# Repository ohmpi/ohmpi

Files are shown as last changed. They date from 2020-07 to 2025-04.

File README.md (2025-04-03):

# OhmPi

Development of a low-cost multi-electrodes resistivity meter for electrical resistivity mesaurement for lab applications, based on raspberry board.

Join the community on [Discord](https://discord.gg/2SCKQZBzXh) to share your experience and provide feedback or use the gitlab issue.

## Installation

1. Download a .zip of this repository (or use `git clone https://gitlab.com/ohmpi/ohmpi.git`)
2. Enter the repository (`cd path/to/ohmpi`) and install the software needed. We made a simple script to make it simpler:

`./install.sh`

The installation script will create a virtual python environement `ohmpy` (with a 'y' at the end) where all packages specified in *requirements.txt* will be installed. The script also takes care of creating a configuration for your hardware if you wish.

To activate the environment and set the necessary `$PYTHONPATH` variable, you can use:

`source env.sh`

More examples are provided in the **[documentation](https://ohmpi.gitlab.io/ohmpi/)**.

## Gallery

A few pictures of the components of the OhmPi. More in the [**DOCUMENTATION**](https://ohmpi.gitlab.io/ohmpi/)!

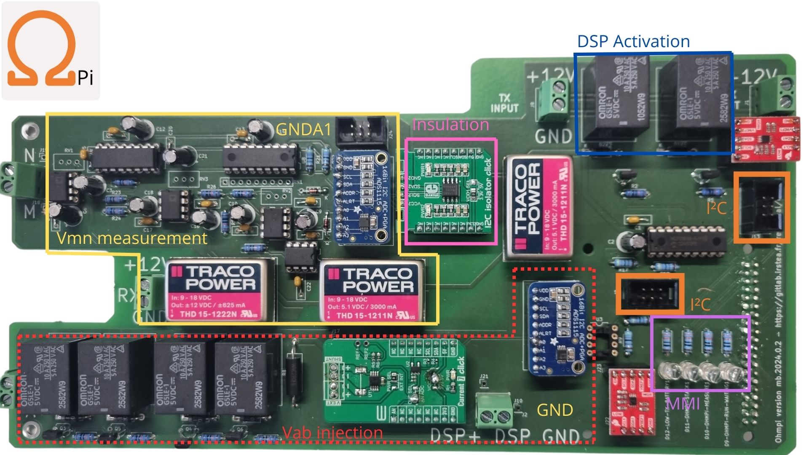
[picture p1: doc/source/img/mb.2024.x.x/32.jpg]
measurment board

*Measurement board (v2024).*

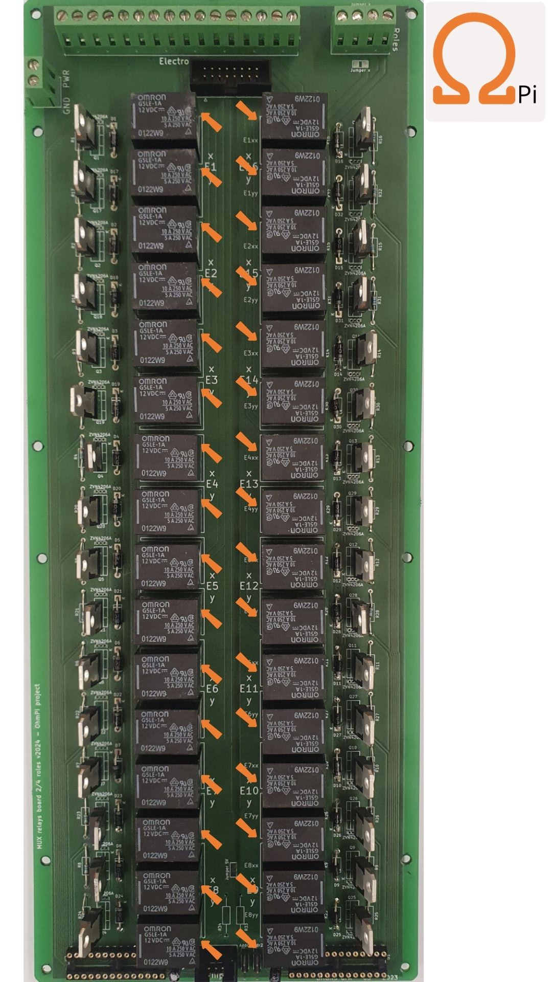
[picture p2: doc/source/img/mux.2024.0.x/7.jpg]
multiplexer board

*Multiplexer board (v2024).*

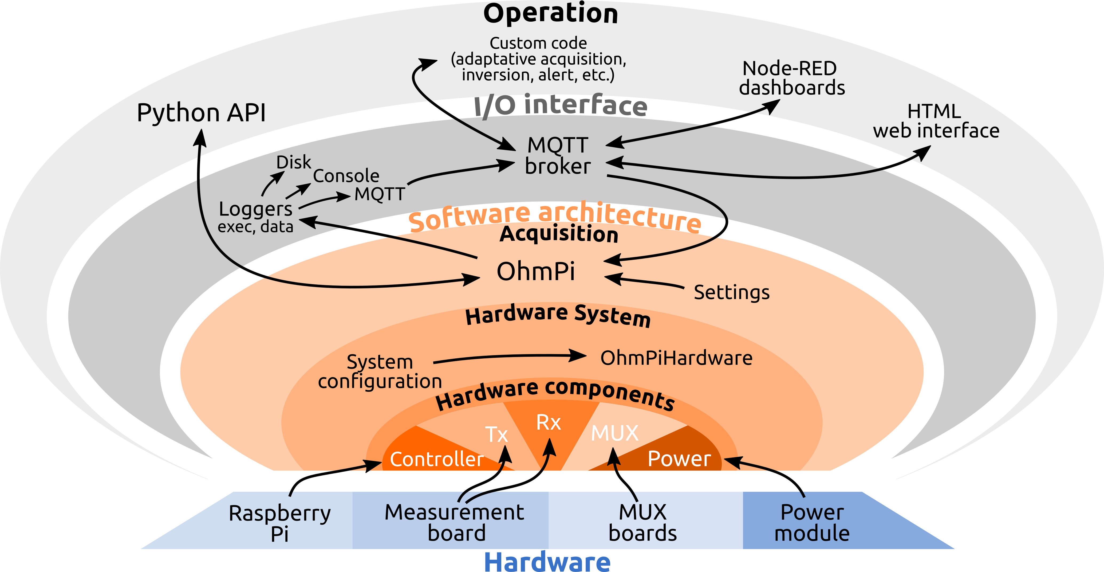
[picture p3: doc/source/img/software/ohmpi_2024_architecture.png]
software architecure

*Software architecture.*

## How to contribute

You can contribute to the code of OhmPi directly in this repository by raising issue or making merge request. We use different branches to manage different readiness level of the code:
- `issue_XXX` (e.g. `issue_240`) is a branch linked to an issue number to develop a new feature or fix a bug.
- `alpha`: experimental version of the code to be tested by core developers, this branch contains the latest changes but is **unstable**.
- `beta`: **testing** version, more stable than `alpha` that can be tried out by contributors to provide feedback to core developpers (released in winter). 
- `rc`: **release candidate** branch, version to be extensively tested before being released and merged into the `master` branch (released in spring).
- `master`: more **stable** version of the code. Bug fixes can be merged directly to master.

You can also contribute to the **documentation** (on the `docs` branch) by improving the documentation or showcasing your OhmPi application.

## Citing Ohmpi

If you use OhmPi for you work, please cite [this paper](https://www.sciencedirect.com/science/article/pii/S2468067220300316) as:

    Rémi Clement, Yannick Fargier, Vivien Dubois, Julien Gance, Emile Gros, Nicolas Forquet, OhmPi: An open source data logger for 
    dedicated applications of electrical resistivity imaging at the small and laboratory scale, HardwareX, Volume 8, 2020, e00122, ISSN 2468-0672, https://doi.org/10.1016/j.ohx.2020.e00122..

## License information

You may redistribute and modify this documentation and make products using it under the terms of the CERN-OHL-P v2 (https://cern.ch/cern-ohl). This documentation is distributed WITHOUT ANY EXPRESS OR IMPLIED WARRANTY, INCLUDING OF MERCHANTABILITY, SATISFACTORY QUALITY AND FITNESS FOR A PARTICULAR PURPOSE. Please see the CERN-OHL-P v2 for applicable conditions

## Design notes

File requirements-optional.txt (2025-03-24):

RPi.GPIO
adafruit-blinka
adafruit-circuitpython-ads1x15
adafruit-circuitpython-tca9548a
adafruit-circuitpython-mcp230xx
adafruit_extended_bus
minimalmodbus
gpiozero
numpy
paho-mqtt==1.6.1
urllib3
termcolor
pandas
matplotlib
scipy
requests
psutil
joblib

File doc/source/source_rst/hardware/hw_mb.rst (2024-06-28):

Measurement board
=============================

This section introduces the OhmPi measurement boards. Starting from this year, it has been possible to use any measurement board with the latest OhmPi code.
Consequently, the OhmPi group provides a variety of board options tailored to your technical needs (e.g., laboratory measurement, field measurement), budget, and electronic skills.

The characteristics of each measurement board are described in the following table:

Recognize the version of the measurement board
----------------------------------------------

   +-----------------------------------------------------------------+
   |   
   |      :width: 900px                                              |
   +-----------------------------------------------------------------+
   |**Measurement board V2023.0.1**                                  |
   +-----------------------------------------------------------------+
   |   
   |      :width: 900px                                              |
   +-----------------------------------------------------------------+
   |**Measurement board V2024.0.2**                                  |
   +-----------------------------------------------------------------+  

Specifications
--------------

.. table::
   :align: center

   +----------------------------------+-----------------------+-----------------------+-----------+
   | **Parameters**                   |**v2023.0.1**          |       **v2024.0.2**   | Units     |
   +==================================+=======================+=======================+===========+
   |Vmn number of channels            |1                      |1                      |-          |
   +----------------------------------+-----------------------+-----------------------+-----------+
   |Operating temperature             |0 to 50                |-25 to 50              |°C         |
   +----------------------------------+-----------------------+-----------------------+-----------+
   |Max. permissible Vab              |24                     |200                    |vdc        |
   +----------------------------------+-----------------------+-----------------------+-----------+
   |Power supply                      |12                     |12                     |vdc        |
   +----------------------------------+-----------------------+-----------------------+-----------+
   |Current with 2 ohms shunt resistor|0.11 to 40             |0.11 to 500            |mA         |
   +----------------------------------+-----------------------+-----------------------+-----------+
   |Min pulse duration                |50                     |50                     |ms         |
   +----------------------------------+-----------------------+-----------------------+-----------+
   |Max pulse duration                |15                     |15                     |second     |
   +----------------------------------+-----------------------+-----------------------+-----------+
   |Vmn input impedance               |80                     |1000                   |MOhm       |
   +----------------------------------+-----------------------+-----------------------+-----------+
   |Vmn range                         |-/+ 5                  | -/+5                  |volt       |
   +----------------------------------+-----------------------+-----------------------+-----------+

Assemble measurement board (MB)
------------------------------- 

.. toctree:: 
   :maxdepth: 2 

   mb/mb_2023.rst
   mb/mb_2024.rst

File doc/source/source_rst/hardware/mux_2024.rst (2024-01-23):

.. warning::
    **OhmPi is a participative project open to all, it requires skills in electronics and to respect the safety rules. OhmPi must be assembled in a professional context and by people competent in electronics. The OhmPi team cannot be held responsible for any material or human damage which would be associated with the use or the assembly of OHMPI. The OhmPi team cannot be held responsible if the equipment does not work after assembly.**

MUX board v2024
****************************************************

The MUX board v2024 uses the same technology than the MUX board v2023, i.e. mechanical multiplexing. However it introduces
a new level of flexibility by addressing multiple roles (A, B, M, N), which allows to build OhmPi system with multiple of 8 electrodes.
Users can physically configure the MUX board to address 2 roles (A, B or M, N) or 4 roles (A, B, M, N). With only 32 relays,
it can address 16 or 8 electrodes, for the 2- and 4-role configuration respectively.
Given the reduced number of relays, the MUX board v2024 is interfaced with only two MCP23017 I/O expanders.
This means that up to 4 MUX boards v2024 (i.e. 32-electrode system) can be directly connected to a measurement board v2024.
A newly introduced I2C extension board (featuring a TCA9548A multiplexer) allows to connect up to 32 MUX board v2024, equating to a 256-electrode system.
In theory, up to 8 I2C extension boards can be connected to the measurement board, which would allow to pilot 2048 electrodes.
For obvious practical reasons, such a configuration couldn't be tested and is likely to be limited by the I2C bus being phisically too long,
which would prevent to reach so many GPIOs.
In an effort to mitigate supply shortages, a last addition concerns the power mosfet associated with the relays,
with the possibility to mount two types of components depending on market availability: either ZVN4206A or STP16NF06L.

Here, we will present how to assemble and configure a 32-electrode system, based on 4 MUX-board v2024 set up to address 2 roles / 16 electrodes each.

**PART A** Assembly of MUX board
======================================================

Required components 
----------------------------------------------------

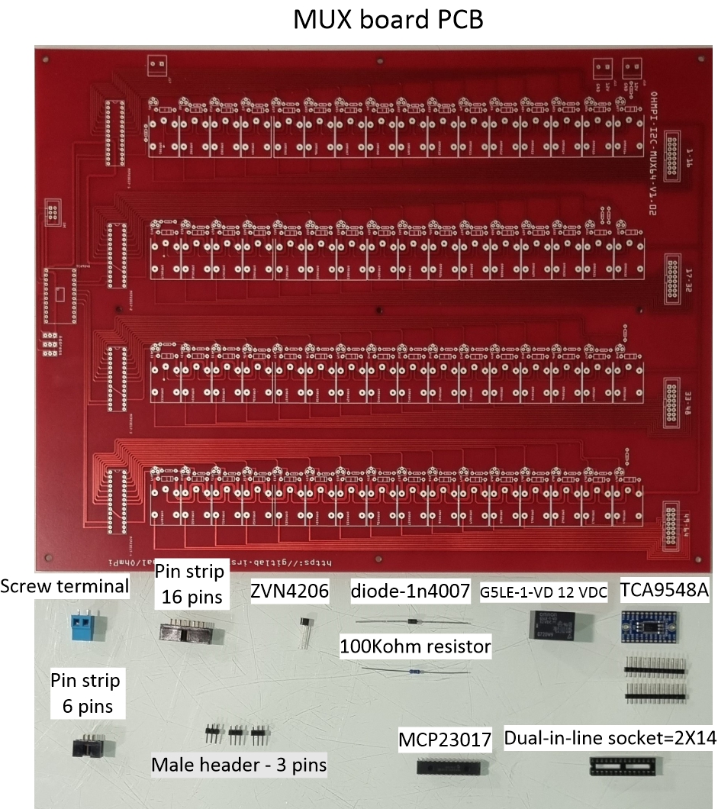
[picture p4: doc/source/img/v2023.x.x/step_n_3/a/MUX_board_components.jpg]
alternate text


.. csv-table:: List of components
   :file: ../../img/v2023.x.x/step_n_3/a/MUX_board_list_2_xx.csv
   :widths: 30, 70, 70, 70, 70, 35, 35
   :header-rows: 1 

.. table::
   :align: center
   
   +--------+--------------------------------------------------------------------------------+
   |        |   
   |      1 +--------------------------------------------------------------------------------+
   |        |Mux board pcb                                                                   | 
   |        |                                                                                |                                                                       
   +--------+--------------------------------------------------------------------------------+

.. table::
   :align: center
   
   +--------+------------------------------------------------------------+
   |        |   
   |      2 +------------------------------------------------------------+
   |        |Installation of the 100 kOhm resistors                      |
   |        |                                                            |                                                                       
   +--------+------------------------------------------------------------+   
   
.. table::
   :align: center
   
   +--------+------------------------------------------------------------+
   |        |   
   |      3 +------------------------------------------------------------+
   |        |Installation of the MOSFET ZVN4206A                         |
   |        |                                                            |                                                                       
   +--------+------------------------------------------------------------+      

.. table::
   :align: center
   
   +--------+------------------------------------------------------------+
   |        |   
   |      4 +------------------------------------------------------------+
   |        |Installation of the diode 1N4007                            |
   |        |                                                            |                                                                       
   +--------+------------------------------------------------------------+    
   
.. table::
   :align: center
   
   +--------+------------------------------------------------------------+
   |        |   
   |      5 +------------------------------------------------------------+
   |        |Installation of the relay                                   | 
   |        |                                                            |                                                                       
   +--------+------------------------------------------------------------+  

.. table::
   :align: center
   
   +--------+------------------------------------------------------------+
   |        |   
   |      6 +------------------------------------------------------------+
   |        |Installation of the terminal screw                          | 
   |        |                                                            |                                                                       
   +--------+------------------------------------------------------------+

.. table::
   :align: center
   
   +--------+------------------------------------------------------------+
   |        |   
   |      7 +------------------------------------------------------------+
   |        |Installation of generic male header                         | 
   |        |                                                            |                                                                       
   +--------+------------------------------------------------------------+ 

.. table::
   :align: center
   
   +--------+------------------------------------------------------------+
   |        |   
   |      8 +------------------------------------------------------------+
   |        |Installation of Pin strip (6 pins)  and pin strip (16 pins) | 
   |        |                                                            |                                                                       
   +--------+------------------------------------------------------------+  

.. table::
   :align: center
   
   +--------+------------------------------------------------------------+
   |        |   
   |      9 +------------------------------------------------------------+
   |        |Installation of DIP Dual In Line Socket 2*14                | 
   |        |                                                            |                                                                       
   +--------+------------------------------------------------------------+  

.. table::
   :align: center
   
   +--------+------------------------------------------------------------+
   |        |   
   |     10 +------------------------------------------------------------+
   |        |Installation of Adafruit TCA9548A                           | 
   |        |                                                            |                                                                       
   +--------+------------------------------------------------------------+

.. table::
   :align: center
   
   +--------+------------------------------------------------------------+
   |        |   
   |     10 +------------------------------------------------------------+
   |        |Installation of MCP23017                                    | 
   |        |                                                            |                                                                       
   +--------+------------------------------------------------------------+  
   
.. note:: 
     This step must be duplicated 4 times for every Mux card.

**PART B** MUX board address
====================================================== 
A MUX v2024 comes with 2 I/O expanders (MCP23017) addressing 16 relays each. They can be identified by the Raspberry Pi unit
with their I2C address ranging 0x20 - 0x27. Two jumpers allow to shift the addresses two by two based on the following combination:

+-------------+-----------------+------------------+
| addresses   | Addr1 position  |  Addr2 position  |
+=============+=================+==================+
| 0x20 - 0x21 |       Up        |       Up         |
+-------------+-----------------+------------------+
| 0x22 - 0x23 |      Down       |       Up         |
+-------------+-----------------+------------------+
| 0x24 - 0x25 |       Up        |      Down        |
+-------------+-----------------+------------------+
| 0x26 - 0x27 |      Down       |      Down        |
+-------------+-----------------+------------------+

.. table::
   :align: center
   
   +--------+------------------------------------------------------------+
   |        |   
   |     1  +------------------------------------------------------------+
   |        |Mount the jumpers and note the value of the address and the |
   |        |electrode name on the mux board (A).                        |                                                                       
   |        +------------------------------------------------------------+  
   |        |   
   |        +------------------------------------------------------------+
   |        |Zoom on the jumper                                          | 
   |        |                                                            |   
   +--------+------------------------------------------------------------+   

For the B electrode board, we suggest addressing it with address 0x71:

.. table::
   :align: center
   
   +--------+------------------------------------------------------------+
   |        |   
   |     2  +------------------------------------------------------------+
   |        |Mount the jumpers and note the value of the address and the |
   |        |electrode name on the mux board (B).                        |                                                                       
   |        +------------------------------------------------------------+  
   |        |   
   |        +------------------------------------------------------------+
   |        |Zoom on the jumper                                          | 
   |        |                                                            |   
   +--------+------------------------------------------------------------+ 

For the N electrode board, we suggest addressing it with address 0x72:

.. table::
   :align: center
   
   +--------+------------------------------------------------------------+
   |        |   
   |     3  +------------------------------------------------------------+
   |        |Mount the jumpers and note the value of the address and the |
   |        |electrode name on the mux board (B).                        |                                                                     
   |        +------------------------------------------------------------+  
   |        |   
   |        +------------------------------------------------------------+
   |        |Zoom on the jumper                                          | 
   |        |                                                            |   
   +--------+------------------------------------------------------------+ 

For the M electrode board, we suggest addressing it with address 0x73: 
  
.. table::
   :align: center
   
   +--------+------------------------------------------------------------+
   |        |   
   |     4  +------------------------------------------------------------+
   |        |Mount the jumpers and note the value of the address and the |
   |        |electrode name on the mux board (B).                        |                                                                     
   |        +------------------------------------------------------------+  
   |        |   
   |        +------------------------------------------------------------+
   |        |Zoom on the jumper                                          | 
   |        |                                                            |   
   +--------+------------------------------------------------------------+    

**PART C** Validation of MUX board
======================================================
The first step is to test the Mux boards before assembling them definitively.
To test the Mux boards, it will be necessary first to make a simplified assembly of the Mux board and the measurement board.

The first thing to do is to prepare a 50 cm long flat wire with two 6-poles connectors.

   +--------+-----------------------------------------------------------------+
   |        |   
   |     1  +-----------------------------------------------------------------+
   |        |Build a cable with 6 contacts with 6 pins connector.             |
   |        |                                                                 |                                                                     
   +--------+-----------------------------------------------------------------+ 
 
   +--------+-----------------------------------------------------------------+
   |        |   
   |     2  +-----------------------------------------------------------------+
   |        |Prepare the measurement board and the first mux board by         |
   |        |example the card with address 0x71.                              |                                                                     
   +--------+-----------------------------------------------------------------+

   +--------+-----------------------------------------------------------------+
   |        |   
   |     3  +-----------------------------------------------------------------+
   |        |Connect the 12V power supply cables to the MUX board             |
   |        |without powering the board.                                      |                                                                     
   +--------+-----------------------------------------------------------------+   

   +--------+------------------------------------------------------------------+
   |        |   
   |     4  +------------------------------------------------------------------+
   |        |Connect the 12V power supply screw terminal of the mux            |
   |        |board to the 12V screw terminal power supply of the               |
   |        |measurement board.                                                |
   +--------+------------------------------------------------------------------+   

   +--------+------------------------------------------------------------------+
   |        |   
   |     5  +------------------------------------------------------------------+
   |        |Connect the 6-contact cable                                       |
   |        |                                                                  |                                                                     
   +--------+------------------------------------------------------------------+

Start your 12V power supply, the raspberry must start. 

Run the terminal and write:

 .. code-block:: python

     i2cdetect -y 1

Three addresses should appear, including the address of the MUX board you have selected. This implies that your board has been detected.

Open the script called "test_mux_board.py".

Run the script

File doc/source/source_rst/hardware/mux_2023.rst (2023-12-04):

.. warning::
    **OhmPi is a participative project open to all, it requires skills in electronics and to respect the safety rules. OhmPi must be assembled in a professional context and by people competent in electronics. The OhmPi team cannot be held responsible for any material or human damage which would be associated with the use or the assembly of OHMPI. The OhmPi team cannot be held responsible if the equipment does not work after assembly.**

MUX board v2023
****************************************************
The multiplexing of the channels is a mechanical multiplexing based on OMRON's manufacturing relays (G5LE-1-VD 12 VDC). Each relay is combined with 
a ZVN4206A power MOFSET. The raspberry has only 30 GPIOs, which is not enough to activate all the 64 electrodes, which represent 512 GPIOs. 
We used gpio expander I2C (MCP23017). We have associated these components with an I2C multiplexer of type type TCA9548A from adafruit.
This combination allows to go up to 512 GPIOs and up to 128 electrodes. Each card has its own digital address between 0X70 and 0X77. 
In the following presentation for an OhmPi 64 electrodes, we will use the addresses 0X70 for channel A, 0X71 for channel B, 0X72 for channel M and 0X73 for channel N.
0X73 for the N channel. 4 MUX board will be needed to multiplex an OhmPi 64 electrodes.

**PART A** Assembly of MUX board
======================================================

Required components 
----------------------------------------------------

alternate text

.. csv-table:: List of components
   :file: ../hardware/mb/MUX_board_2023.csv
   :widths: 30, 70, 70, 70, 70, 35, 35,1
   :header-rows: 1 

.. table::
   :align: center
   
   +--------+--------------------------------------------------------------------------------+
   |        |   
   |      1 +--------------------------------------------------------------------------------+
   |        |Mux board pcb                                                                   | 
   |        |                                                                                |                                                                       
   +--------+--------------------------------------------------------------------------------+

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

.. table::
   :align: center
   
   +--------+------------------------------------------------------------+
   |        |   
   |      6 +------------------------------------------------------------+
   |        |Installation of the terminal screw                          | 
   |        |                                                            |                                                                       
   +--------+------------------------------------------------------------+

.. table::
   :align: center
   
   +--------+------------------------------------------------------------+
   |        |   
   |      7 +------------------------------------------------------------+
   |        |Installation of generic male header                         | 
   |        |                                                            |                                                                       
   +--------+------------------------------------------------------------+ 

.. table::
   :align: center
   
   +--------+------------------------------------------------------------+
   |        |   
   |      8 +------------------------------------------------------------+
   |        |Installation of Pin strip (6 pins)  and pin strip (16 pins) | 
   |        |                                                            |                                                                       
   +--------+------------------------------------------------------------+  

.. table::
   :align: center
   
   +--------+------------------------------------------------------------+
   |        |   
   |      9 +------------------------------------------------------------+
   |        |Installation of DIP Dual In Line Socket 2*14                | 
   |        |                                                            |                                                                       
   +--------+------------------------------------------------------------+  

.. table::
   :align: center
   
   +--------+------------------------------------------------------------+
   |        |   
   |     10 +------------------------------------------------------------+
   |        |Installation of Adafruit TCA9548A                           | 
   |        |                                                            |                                                                       
   +--------+------------------------------------------------------------+

.. table::
   :align: center
   
   +--------+------------------------------------------------------------+
   |        |   
   |     10 +------------------------------------------------------------+
   |        |Installation of MCP23017                                    | 
   |        |                                                            |                                                                       
   +--------+------------------------------------------------------------+  
   
.. note:: 
     This step must be duplicated 4 times for every Mux card.

**PART B** MUX board address
====================================================== 
To build an ohmpi it is necessary to have 4 MUX boards, with 4 different addresses. It is therefore necessary to identify each board, by assigning an address, which will be allocated in the OhmPi code.
We present here the addresses selected by default.

For the A electrode board, we suggest addressing it with address 0x70:

.. table::
   :align: center
   
   +--------+------------------------------------------------------------+
   |        |   
   |     1  +------------------------------------------------------------+
   |        |Mount the jumpers and note the value of the address and the |
   |        |electrode name on the mux board (A).                        |                                                                       
   |        +------------------------------------------------------------+  
   |        |   
   |        +------------------------------------------------------------+
   |        |Zoom on the jumper                                          | 
   |        |                                                            |   
   +--------+------------------------------------------------------------+   

For the B electrode board, we suggest addressing it with address 0x71:

.. table::
   :align: center
   
   +--------+------------------------------------------------------------+
   |        |   
   |     2  +------------------------------------------------------------+
   |        |Mount the jumpers and note the value of the address and the |
   |        |electrode name on the mux board (B).                        |                                                                       
   |        +------------------------------------------------------------+  
   |        |   
   |        +------------------------------------------------------------+
   |        |Zoom on the jumper                                          | 
   |        |                                                            |   
   +--------+------------------------------------------------------------+ 

For the N electrode board, we suggest addressing it with address 0x72:

.. table::
   :align: center
   
   +--------+------------------------------------------------------------+
   |        |   
   |     3  +------------------------------------------------------------+
   |        |Mount the jumpers and note the value of the address and the |
   |        |electrode name on the mux board (B).                        |                                                                     
   |        +------------------------------------------------------------+  
   |        |   
   |        +------------------------------------------------------------+
   |        |Zoom on the jumper                                          | 
   |        |                                                            |   
   +--------+------------------------------------------------------------+ 

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

**PART C** Validation of MUX board
======================================================
The first step is to test the Mux boards before assembling them definitively.
To test the Mux boards, it will be necessary first to make a simplified assembly of the Mux board and the measurement board.

The first thing to do is to prepare a 50 cm long flat wire with two 6-poles connectors.

   +--------+-----------------------------------------------------------------+
   |        |   
   |     1  +-----------------------------------------------------------------+
   |        |Build a cable with 6 contacts with 6 pins connector.             |
   |        |                                                                 |                                                                     
   +--------+-----------------------------------------------------------------+ 
 
   +--------+-----------------------------------------------------------------+
   |        |   
   |     2  +-----------------------------------------------------------------+
   |        |Prepare the measurement board and the first mux board by         |
   |        |example the card with address 0x71.                              |                                                                     
   +--------+-----------------------------------------------------------------+

   +--------+-----------------------------------------------------------------+
   |        |   
   |     3  +-----------------------------------------------------------------+
   |        |Connect the 12V power supply cables to the MUX board             |
   |        |without powering the board.                                      |                                                                     
   +--------+-----------------------------------------------------------------+   

   +--------+------------------------------------------------------------------+
   |        |   
   |     4  +------------------------------------------------------------------+
   |        |Connect the 12V power supply screw terminal of the mux            |
   |        |board to the 12V screw terminal power supply of the               |
   |        |measurement board.                                                |
   +--------+------------------------------------------------------------------+   

   +--------+------------------------------------------------------------------+
   |        |   
   |     5  +------------------------------------------------------------------+
   |        |Connect the 6-contact cable                                       |
   |        |                                                                  |                                                                     
   +--------+------------------------------------------------------------------+

Start your 12V power supply, the raspberry must start. 

Run the terminal and write:

 .. code-block:: python

     i2cdetect -y 1

Three addresses should appear, including the address of the MUX board you have selected. This implies that your board has been detected.

Open the script called "test_mux_board.py".

Run the script

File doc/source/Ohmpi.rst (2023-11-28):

*************** 
OhmPi project 
***************

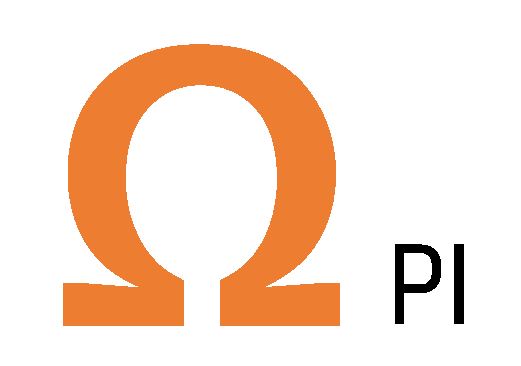
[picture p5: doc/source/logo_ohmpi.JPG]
Logo OhmPi
    

|  

**Authors:** 
------------
| Rémi CLEMENT, Vivien DUBOIS, Nicolas Forquet, INRAE, REVERSAAL, Villeurbanne, France
| Olivier KAUFMANN, Arnaud WATLET, Université de Mons, Mons, Belgium
| Yannick FARGIER, GERS-RRO, Univ Gustave Eiffel, IFSTTAR, Lyon, France
| Hélène GUYARD, IGE Grenoble, Université Grenoble Alpes, Grenoble, France
| Guillaume BLANCHY, ILVO, Merelbeke, Belgium

**Partners:**
-------------

.. table::
   :align: center
  
   +-------------------------------------------------+--------------------------------------------------+----------------------------------------------+
   |   
   +-------------------------------------------------+--------------------------------------------------+----------------------------------------------+
   |   
   +-------------------------------------------------+--------------------------------------------------+----------------------------------------------+

**Citing OhmPi:** 
-----------------

|

*Rémi Clement, Yannick Fargier, Vivien Dubois, Julien Gance, Emile Gros, et al.. OhmPi: An open*
*source data logger for dedicated applications of electrical resistivity imaging at the small and laboratory*
*scale. HardwareX, Elsevier, 2020, 8, 24 p. ff10.1016/j.ohx.2020.e00122ff.*

|
   
**Introduction :** 
------------------

.. warning::
    OhmPi is a participative project open to all, it requires skills in electronics and to respect the safety rules. 
    OhmPi must be assembled in a professional context and by people competent in electronics. The OhmPi team cannot be
    held responsible for any material or human damage which would be associated with the use or the assembly of OhmPi. 
    The OhmPi team cannot be held responsible if the equipment does not work after assembly. You may redistribute and 
    modify this documentation and make products using it under the terms of the CERN-OHL-P v2. This documentation is 
    distributed WITHOUT ANY EXPRESS OR IMPLIED WARRANTY, INCLUDING OF MERCHANTABILITY, SATISFACTORY QUALITY AND FITNESS
     FOR A PARTICULAR PURPOSE. Please see the CERN-OHL-P v2 for applicable conditions.

This documentation presents the development of a low-cost, open hardware \ 
resistivity meter to provide the scientific community with a robust \
and flexible tool for small-scale experiments. Called OhmPi, this basic resistivity meter\
features current injection and measurement functions associated with a multiplexer \
that allows performing automatic measurements with up to 64 electrodes.\
OhmPi's philosophy is to provide a fully open source and open hardware tool\
to the near surface scientific community.

.. note:: 
   Anyone who wants to get involved is welcome to join the OhmPi project!

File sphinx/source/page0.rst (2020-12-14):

*************** 
Premiere page 
***************
 
**OhmPi project** 
************************* 
 
Logo OhmPi

Authors: 

| Rémi CLEMENT,Vivien DUBOIS,Nicolas Forquet, INRAE, REVERSAAL, F-69626, Villeurbanne Cedex, France.
| Yannick FARGIER, GERS-RRO, Univ Gustave Eiffel, IFSTTAR, Univ Lyon, F-69675 Lyon, France.
| Julien GANCE, IRIS Instruments, 45100 Orléans, France.
| Hélène GUYARD, IGE Grenoble, Université Grenoble Alpes, Grenoble.

Parteners:

.. table::
   :align: center
  
   +-------------------------------+-----------------------------------+-------------------------------+-----------------------------------+
   |   
   +-------------------------------+-----------------------------------+-------------------------------+-----------------------------------+

Creation date : Juillet 2020.

Update : 21 août 2020.

Status of document: In progress.

**Citing OhmPi** 
=========================
*Rémi Clement, Yannick Fargier, Vivien Dubois, Julien Gance, Emile Gros, et al.. OhmPi: An open*
*source data logger for dedicated applications of electrical resistivity imaging at the small and laboratory*
*scale. HardwareX, Elsevier, 2020, 8, 24 p. ff10.1016/j.ohx.2020.e00122ff.*
   
**Introduction to OhmPi** 
=========================

This documentation presents the development of a low-cost, open hardware \ 
resistivity meter to provide the scientific community with a robust \
and flexible tool for small-scale experiments. Called OhmPi, this basic resistivity meter\
features current injection and measurement functions associated with a multiplexer \
that allows performing automatic measurements with up to 32 electrodes.\ 
OhmPi's philosophy is to provide a fully open source and open hardware tool /
to the near surface scientific community.

.. note:: 
   Everyone willing to get involved is  welcome in OhmPi Project!.

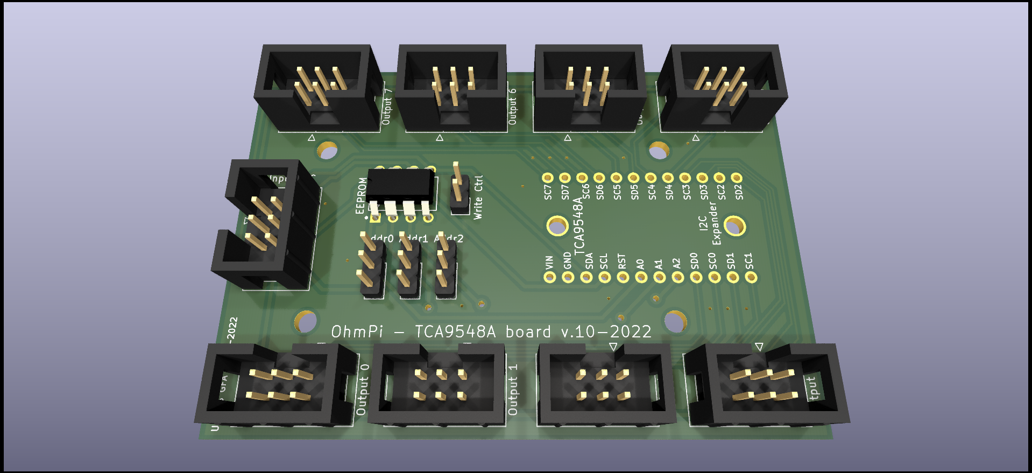
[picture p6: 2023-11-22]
PCB_boards/accessories/i2c_ext.2024.0.0/TCA_board_2.png

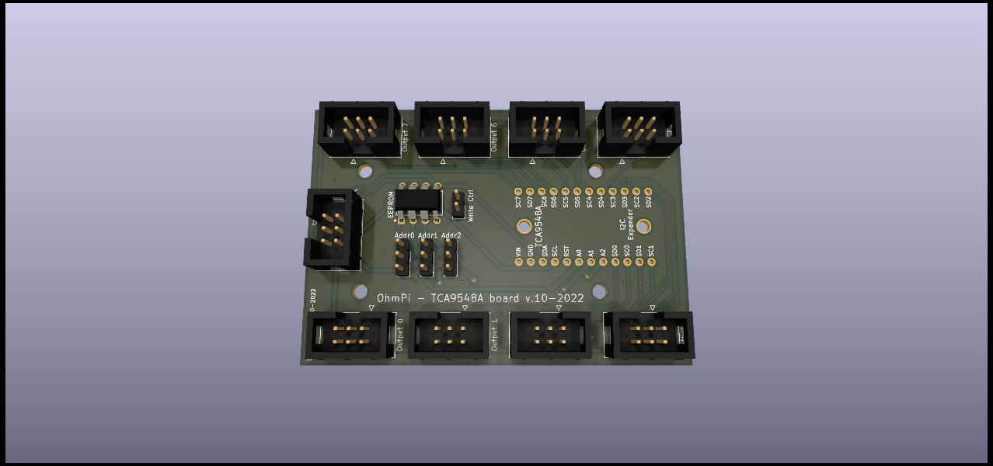
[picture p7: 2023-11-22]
PCB_boards/accessories/i2c_ext.2024.0.0/MUX_v2024_tca_board.png

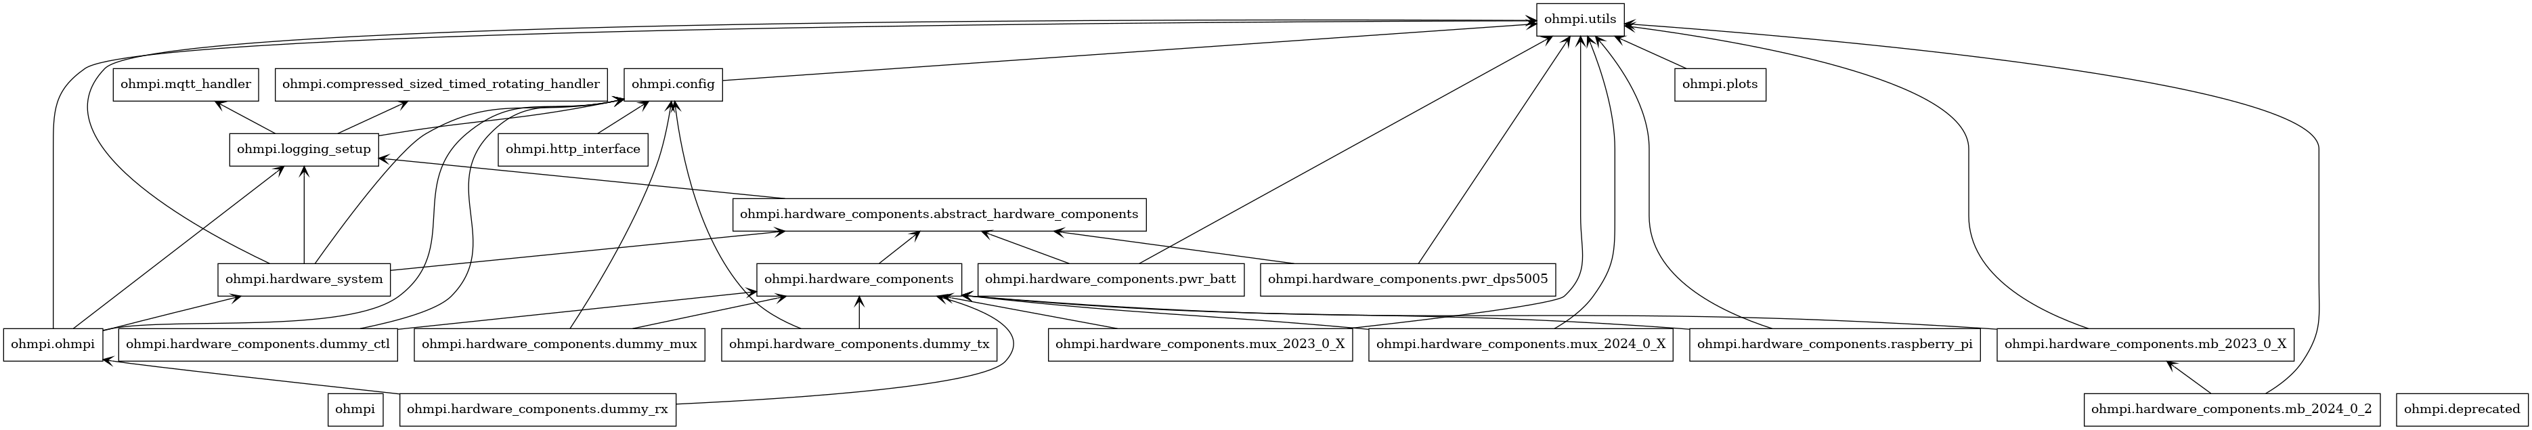
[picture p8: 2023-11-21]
uml_diagrams/packages_uml_ohmpi.dot.png

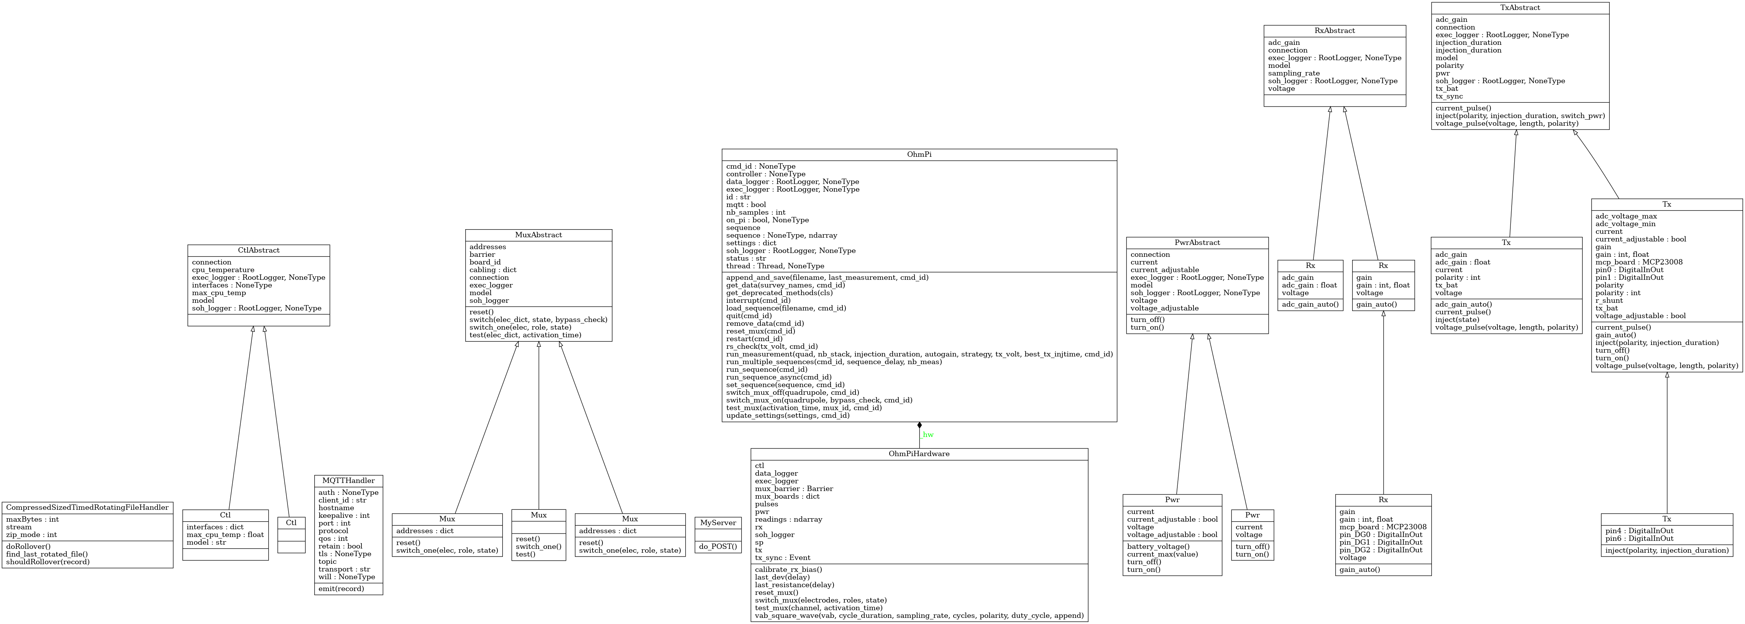
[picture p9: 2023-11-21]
uml_diagrams/classes_uml_ohmpi.dot.png

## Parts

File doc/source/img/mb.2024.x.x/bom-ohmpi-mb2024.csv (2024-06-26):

Component | Quantity | Cost per unit | Mouser ref | Manufacturer | Manufacturer reference | Description | Web link | Total cost EUR excl.VAT
100 kOhm resistor | 13 | 0.223 | 594-5063JD100K0FT | MBA02040C1003FRP00 | Vishay | Metal Film Resistors - Through Hole .4watt 100Kohms 1% 1/8watt body size | https://eu.mouser.com/ProductDetail/Vishay-Beyschlag/MBA02040C1003FRP00?qs=mzRxyRlhVdt9crF7Zyf%2F5Q%3D%3D | 2.899
330 Ohms resistor | 4 | 0.307 | 279-CFR100J330R | CFR100J330R | TE Connectivity | Carbon Film Resistors - Through Hole 330Ohm 1W 500PPM | https://eu.mouser.com/ProductDetail/TE-Connectivity-Holsworthy/CFR100J330R?qs=DDevMFOh4ssVKnglsGY0HA%3D%3D | 1.228
4.7 kOhms resistor | 4 | 0.307 | 603-CFR-25JB-52-4K7 | CFR-25JB-52-4K7 | YAGEO | Carbon Film Resistors - Through Hole 1/4W 4.7K Ohm 5% | https://eu.mouser.com/ProductDetail/YAGEO/CFR-25JB-52-4K7?qs=oypCK0zG3252T%2FvSUvCH9g%3D%3D | 1.228
2 ohms shunt resistor | 1 | 1.33 | 588-WNC2R0FET | WNC2R0FET | Ohmite | Wirewound Resistors - Through Hole 2W 2 ohms 1% | https://eu.mouser.com/ProductDetail/Ohmite/WNC2R0FET?qs=CDPnWzNfzJb5BMolBZTI%252Bw%3D%3D | 1.33
50V 1A general purpose rectifier diode DO-41 | 6 | 0.214 | 637-1N4001 | 1N4001 | Diotec | Semiconductor Rectifiers Diode DO-41 50V 1A | https://eu.mouser.com/ProductDetail/Diotec-Semiconductor/1N4001?qs=OlC7AqGiEDlll8NA510wmA%3D%3D | 1.284
cree LED | 4 | 0.279 | 941-C503BGANCD0E0781 | C503B-GAN-CD0E0781 | Cree LED | Standard LEDs - Through Hole Green LED 527nm 5-mmRound 32900-64600mcd | https://eu.mouser.com/ProductDetail/Cree-LED/C503B-GAN-CD0E0781?qs=7D1LtPJG0i1J7Dm%252B%252B5IGZw%3D%3D | 1.116
50V 0.2 A small signal schottky diode DO-35 | 2 | 0.437 | 771-BAT86113 | BAT86 113 | Nexperia | Schottky Diodes & Rectifiers BAT86/SOD68/DO-34 | https://eu.mouser.com/ProductDetail/Nexperia/BAT86113?qs=me8TqzrmIYX1ahcmZsx1tg%3D%3D | 0.874
OP27E (single ultra offset 8DIP) | 3 | 9.53 | 584-OP27EPZ | OP27EPZ | Analog Devices Inc. | Precision Amplifiers LOW-NOISE PRECISION OP AMP | https://eu.mouser.com/ProductDetail/Analog-Devices/OP27EPZ?qs=WIvQP4zGangDp3uWiH2URA%3D%3D | 28.59
MCP23008 (GPIO expander) | 2 | 1.89 | 485-593 | 593 | Adafruit | Adafruit Accessories MCP23008 - i2c 8 input/output port expander | https://eu.mouser.com/ProductDetail/Adafruit/593?qs=GURawfaeGuAf08zux7w%2FuQ%3D%3D | 3.78
ADS1115 adafruit board (pack of 3) | 2 | 14.9 | 485-1085 | 1085 | Adafruit | Data Conversion IC Development Tools ADS1115 16-Bit ADC - 4 Channel with Programmable Gain Amplifier | https://www.amazon.fr/AZDelivery-ADS1115-Parent-3X/dp/B07QHWLTTS?__mk_fr_FR=%C3%85M%C3%85%C5%BD%C3%95%C3%91 | 14.99
2.5V precision voltage reference | 1 | 6.12 | 584-REF03GPZ | REF03GPZ | Analog Devices Inc. | Voltage References PRECISION LOW-COST 2.5V R | https://eu.mouser.com/ProductDetail/Analog-Devices/REF03GPZ?qs=WIvQP4zGangjpDFoUwu1Bw%3D%3D | 6.12
DG411DJ analog switch | 1 | 2.23 | 781-DG411DJ-E3 | DG411DJ-E3 | Vishay | Analog Switch ICs HIGH SPEED DG411 DIP-16 | https://eu.mouser.com/ProductDetail/Vishay-Semiconductors/DG411DJ-E3?qs=xkjjIvogybzZNZq%252BuWCW1Q%3D%3D | 2.23
unpolar capacitor 100nF | 12 | 0.214 | 594-K104K15X7RF5UL2 | K104K15X7RF5UL2 | Vishay | Multilayer Ceramic Capacitors MLCC - Leaded K 50V 100NF +/- 10 % X7R AMMO E3 | https://eu.mouser.com/ProductDetail/Vishay-BC-Components/K104K15X7RF5UL2?qs=rLgk8CAOBHbCqsnkGO2HJA%3D%3D | 2.568
polarized capacitor 10uF | 10 | 0.27 | 667-EEU-EB1J100S | EEU-EB1J100S | Panasonic | Aluminum Electrolytic Capacitors - Radial Leaded 10uF 63volts AEC-Q200 | https://eu.mouser.com/ProductDetail/Panasonic/EEU-EB1J100S?qs=cEAFgkeRviBcbEMSGHCq5g%3D%3D | 2.7
N channel 60V 600mA 700mW through hole transistor (ZVN4206ASTZ) | 6 | 0.335 | 522-ZVN4206ASTZ | ZVN4206ASTZ | Diodes Incorporated | MOSFET N-Chnl 60V | https://www.mouser.be/ProductDetail/onsemi-Fairchild/2N7000BU?qs=k2x4EL1%2FKj6oeXMHAfSm5A%3D%3D | 2.01
THD1512 11N (output 5V) | 2 | 48.53 | 495-THD15-1211N | THD 15-1211N | TRACO Power | Isolated DC/DC Converters - Through Hole Product Type: DC/DC, Package Style: DIP-24, Output Power (W): 15, Input Voltage: 9-18 VDC, Output 1 (Vdc): 5.1, Output 2 (Vdc): N/A, Output 3 (Vdc): N/A | https://eu.mouser.com/ProductDetail/TRACO-Power/THD-15-1211N?qs=ckJk83FOD0X2IyoEoPcnmg%3D%3D | 97.06
THD1512 22N (output 12V) | 1 | 52 | 495-THD-15-1222N | THD 15-1222N | TRACO Power | Isolated DC/DC Converters - Through Hole Product Type: DC/DC, Package Style: DIP-24, Output Power (W): 15, Input Voltage: 9-18 VDC, Output 1 (Vdc): 12, Output 2 (Vdc): -12, Output 3 (Vdc): N/A | https://www.mouser.be/ProductDetail/TRACO-Power/THD-15-1222N?qs=ckJk83FOD0UVycxQxcHQFw%3D%3D | 52
terminal block 12V | 6 | 0.848 | 649-VI02215200J0G | VI0221520000G | Amphenol | Fixed Terminal Blocks TB RIS CLA 180 STACK | https://eu.mouser.com/ProductDetail/Amphenol-Anytek/VI0221520000G?qs=Mv7BduZupUi3lmtBYXCXvw%3D%3D | 5.088
mikroe i2C isolator | 1 | 16.74 | 932-MIKROE-1878 | MIKROE-1878 | Mikroe | Interface Development Tools I2C Isolator click | https://eu.mouser.com/ProductDetail/Mikroe/MIKROE-1878?qs=k5OWtXsTJao5L2rHk53Deg%3D%3D | 16.74
mikroe shunt current sensor | 1 | 24.18 | 932-MIKROE-4976 | MIKROE-4976 | Mikroe | Power Management IC Development Tools Current 7 Click | https://eu.mouser.com/ProductDetail/Mikroe/MIKROE-4976?qs=MyNHzdoqoQKaB6t4IH2nAQ%3D%3D | 24.18
SparkFun Accessories Level Translator Breakout | 2 | 4.03 | 474-BOB-15439 | BOB-15439 | SparkFun Electronics | SparkFun Accessories Level Translator Breakout - PCA9306 | https://eu.mouser.com/ProductDetail/SparkFun/BOB-15439?qs=P1JMDcb91o4XoNPr%252B0Xi4g%3D%3D | 0
omhron G5LE relay | 6 | 1.44 | 653-G5LE-1A4-DC5 | G5LE-1A4-DC5 | Omron | General Purpose Relays Power PCB Relay SPST-NO Sealed 5VDC | https://eu.mouser.com/ProductDetail/Omron-Electronics/G5LE-1A4-DC5?qs=pWf36BUtxBgFTk6ytLB7NQ%3D%3D | 8.64
DIP for MCP23008 (18 pins) | 2 | 1.33 | 575-1104731841001000 | 110-47-318-41-001000 | Mill-Max | IC & Component Sockets STANDRD SOLDER TAIL DIP SOCKET | https://eu.mouser.com/ProductDetail/Mill-Max/110-47-318-41-001000?qs=5aG0NVq1C4xxoOYTdZ6dOw%3D%3D | 2.66
DIP for OP27E (8 pins) | 5 | 1.39 | 575-113308 | 110-13-308-41-001000 | Mill-Max | IC & Component Sockets 8P GLD PIN GLD CONT | https://eu.mouser.com/ProductDetail/Mill-Max/110-13-308-41-001000?qs=WZeyYeqMOWeYjIS4tXLt7Q%3D%3D | 6.95
DIP for DG411DJ (16 pins) | 1 | 1.05 | 575-11044316 | 110-44-316-41-001000 | Mill-Max | IC & Component Sockets 16P TIN PIN TIN CONT | https://eu.mouser.com/ProductDetail/Mill-Max/110-44-316-41-001000?qs=IGgAdOvCTsRH%252BXEWrwEHKg%3D%3D | 1.05
header for raspberrypi | 1 | 1.87 | 474-PRT-14017 | PRT-14017 | SparkFun Electronics | Raspberry Pi Accessories Raspberry Pi GPIO Tall Header - 2x20 | https://eu.mouser.com/ProductDetail/SparkFun/PRT-14017?qs=a4BXICGgSn%2F%252BaML822b65A%3D%3D | 1.87
header socket 1 row 5 positions | 2 | 1.97 | 571-5-534237-3 | 5-534237-3 | TE Connectivity | Headers & Wire Housings REC 1X05P VRT T/H | https://eu.mouser.com/ProductDetail/TE-Connectivity/5-534237-3?qs=Eln3I3szM1klmLr%252BSZCsuQ%3D%3D | 3.94
header socket 1 row 4 positions | 3 | 1.46 | 571-5-534237-2 | 5-534237-2 | TE Connectivity | Headers & Wire Housings REC 1X04P VRT T/H | https://eu.mouser.com/ProductDetail/TE-Connectivity/5-534237-2?qs=GYgf5PdsjzkI3hK2O1eiLQ%3D%3D | 4.38
header socket 1 row 8 positions | 4 | 1.74 | 571-5-535541-6 | 5-535541-6 | TE Connectivity | Headers & Wire Housings REC 1X08P VRT T/H | https://eu.mouser.com/ProductDetail/TE-Connectivity/5-535541-6?qs=xDp7PGUNC%252BuqVwKJJvkWQw%3D%3D | 6.96
header socket 1 row 10 positions | 2 | 2.71 | 200-SSW11002GS | SSW-110-02-G-S | Samtec | Headers & Wire Housings Tiger Buy Socket Strip with PCB Tails, .100" Pitch | https://eu.mouser.com/ProductDetail/Samtec/SSW-110-02-G-S?qs=rU5fayqh%252BE0w1ORXZiBQpw%3D%3D | 5.42
header socket 1 row 2 positions | 1 | 1.02 | 200-SSW10202GS | SSW-102-02-G-S | Samtec | Headers & Wire Housings Tiger Buy Socket Strip with PCB Tails, .100" Pitch | https://eu.mouser.com/ProductDetail/Samtec/SSW-102-02-G-S?qs=rU5fayqh%252BE2ZEIMTlw%2FBLw%3D%3D | 1.02
header pins 1 row 10 positions | 1 | 1.24 | 571-1-826629-0 | 1-826629-0 | TE Connectivity | Headers & Wire Housings 10P SINGLE ROW | https://eu.mouser.com/ProductDetail/TE-Connectivity/1-826629-0?qs=FazuUmncXom0aPLI6ZgGxg%3D%3D | 1.24
IDC sockets (go on the ribon cable) | 2 | 0.43 | 710-61200623021 | 61200623021 | Wurth Elektronik | Headers & Wire Housings WR-BHD 2.54mm Female 6P Strt IDC Conn | https://eu.mouser.com/ProductDetail/Wurth-Elektronik/61200623021?qs=PhR8RmCirEabk1Ywkdxzfw%3D%3D | 0.86
IDC pins | 3 | 1.32 | 571-1761681-1 | 1761681-1 | TE Connectivity | Headers & Wire Housings IDC LOW PRO HDR 6P VERT HT BLACK | https://eu.mouser.com/ProductDetail/TE-Connectivity/1761681-1?qs=BqFpTYCQ3dLAeZ2wzdz7aw%3D%3D | 3.96
PCB measurement board (pack of 3) | 1 |  |  |  |  |  | https://aisler.net/?lang=fr-FR | 70
Raspberryp pi 4 | 1 | 63 |  |  |  |  | https://www.kiwi-electronics.com/en/raspberry-pi-4-model-b-4gb-4268?src=raspberrypi | 63
socket to cut for 3 THD | 3 | 1.73 |  |  |  |  | https://www.mouser.be/ProductDetail/Mill-Max/801-47-012-10-012000?qs=5aG0NVq1C4x40xNvDlnKzg%3D%3D | 5.19
10k potentiometer | 2 | optional |  |  |  |  |  | 0
R array sip9 | 1 | optional |  |  |  |  |  | 0
10k potentiometer bournds 3296W_vertical | 1 | optional |  |  |  |  |  | 0

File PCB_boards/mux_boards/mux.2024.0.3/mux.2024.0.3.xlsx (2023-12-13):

Source: | /home/arnaud/projects/ohmpi/MUX_board/2024.0.0/relay_board_32_new/MUX_v2024_relay_board_32.kicad_sch
Date: | Mon 11 Dec 2023 10:51:44 CET
Tool: | Eeschema 7.0.9-7.0.9~ubuntu22.04.1
Generator: | /usr/share/kicad/plugins/bom_csv_grouped_by_value_with_fp.py
Component Count: | 153
Ref | Qnty | Component | Description | Vendor | Alternative vendor | unit price | total price | Total price ZVN
C1, C2 | 2 | 100nF | Unpolarized capacitor, small symbol | https://www.mouser.be/ProductDetail/KEMET/C320C104K1R5TA7303?qs=c4UyoTs%2FLq1th4mcyOeTmA%3D%3D |  | 0.22 € | 0.44 € | 0.44 €
C3, C4 | 2 | 10uF | Polarized capacitor, small symbol | https://www.mouser.be/ProductDetail/Panasonic/ECA-1JHG100B |  | 0.24 € | 0.48 € | 0.48 €
D1, D2, D3, D4, D5, D6, D7, D8, D9, D10, D11, D12, D13, D14, D15, D16, D17, D18, D19, D20, D21, D22, D23, D24, D25, D26, D27, D28, D29, D30, D31, D32 | 32 | 1N_E4007 | 1000V 1A General Purpose Rectifier Diode, DO-41 | https://eu.mouser.com/ProductDetail/Diodes-Incorporated/1N4007-T?qs=e%2FRqmsgwm9iVtgJYUW23AA%3D%3D |  | 0.13 € | 4.16 € | 4.16 €
J1 | 1 | Relays Pwr | Generic screw terminal, single row, 01x02, script generated (kicad-library-utils/schlib/autogen/connector/) |  | https://eu.mouser.com/ProductDetail/TE-Connectivity/282837-2?qs=A%252Bip%252BNCYi6O2H0NGWOeAxg%3D%3D | 0.55 € | 0.55 € | 0.55 €
J2 | 1 | I2C | Generic connector, double row, 02x03, odd/even pin numbering scheme (row 1 odd numbers, row 2 even numbers), script generated (kicad-library-utils/schlib/autogen/connector/) |  | https://eu.mouser.com/ProductDetail/Wurth-Elektronik/61200621621?qs=PhR8RmCirEbjX8n1RKw4Jw%3D%3D | 0.44 € | 0.44 € | 0.44 €
J3 | 1 | Screw_Terminal_01x04 | Generic screw terminal, single row, 01x04, script generated (kicad-library-utils/schlib/autogen/connector/) |  | https://eu.mouser.com/ProductDetail/TE-Connectivity/282837-2?qs=A%252Bip%252BNCYi6O2H0NGWOeAxg%3D%3D | 0.55 € | 1.10 € | 0.55 €
J4 | 1 | Conn_02x08_Odd_Even | Generic connector, double row, 02x08, odd/even pin numbering scheme (row 1 odd numbers, row 2 even numbers), script generated (kicad-library-utils/schlib/autogen/connector/) | https://eu.mouser.com/ProductDetail/Wurth-Elektronik/61201621621?qs=ZtY9WdtwX55qFf4n3EFuaA%3D%3D |  | 0.58 € | 0.58 € | 0.58 €
J5 | 1 | Screw_Terminal_01x16 | Generic screw terminal, single row, 01x16, script generated (kicad-library-utils/schlib/autogen/connector/) |  | https://eu.mouser.com/ProductDetail/TE-Connectivity/282837-2?qs=A%252Bip%252BNCYi6O2H0NGWOeAxg%3D%3D | 0.55 € | 4.40 € | 0.55 €
JP1 | 1 | Addr 2 | Jumper, 3-pole, both open | https://eu.mouser.com/ProductDetail/TE-Connectivity/4-103321-5?qs=5TwgZeq9E7HSYLqaljJYrw%3D%3D |  | 0.17 € | 0.17 € | 0.17 €
JP2 | 1 | Addr 1 | Jumper, 3-pole, both open | https://eu.mouser.com/ProductDetail/TE-Connectivity/4-103321-5?qs=5TwgZeq9E7HSYLqaljJYrw%3D%3D |  | 0.17 € | 0.17 € | 0.17 €
K1, K2, K3, K4, K5, K6, K7, K8, K9, K10, K11, K12, K13, K14, K15, K16, K17, K18, K19, K20, K21, K22, K23, K24, K25, K26, K27, K28, K29, K30, K31, K32 | 32 | G5LE-1A DC12 | Omron G5LE relay, Miniature Single Pole, SPDT, 10A | https://eu.mouser.com/ProductDetail/Omron-Electronics/G5LE-1A-DC12?qs=sGAEpiMZZMsqIr59i2oRcj2o81oJCrqXrP4H3ZdDYK4%3D |  | 1.18 € | 37.76 € | 37.76 €
Q1, Q2, Q3, Q4, Q5, Q6, Q7, Q8, Q9, Q10, Q11, Q12, Q13, Q14, Q15, Q16, Q17, Q18, Q19, Q20, Q21, Q22, Q23, Q24, Q25, Q26, Q27, Q28, Q29, Q30, Q31, Q32 | 32 | STP16NF06 | 30A Id, 50V Vds, N-Channel Power MOSFET, TO-220 | https://eu.mouser.com/ProductDetail/STMicroelectronics/STP16NF06?qs=FOlmdCx%252BAA3QgI0ylnH1gA%3D%3D |  | 1.08 € | 34.56 €
Q1, Q2, Q3, Q4, Q5, Q6, Q7, Q8, Q9, Q10, Q11, Q12, Q13, Q14, Q15, Q16, Q17, Q18, Q19, Q20, Q21, Q22, Q23, Q24, Q25, Q26, Q27, Q28, Q29, Q30, Q31, Q32 | 32 | ZVN4206A | 30A Id, 50V Vds, N-Channel Power MOSFET, TO-220 | https://eu.mouser.com/ProductDetail/Diodes-Incorporated/ZVN4206AVSTZ?qs=%2F4dsY8i%2FUxLhPG5M4pjuJg%3D%3D |  | 0.60 € |  | 19.20 €
R1, R2, R3, R4, R5, R6, R7, R8, R9, R10, R11, R12, R13, R14, R15, R16, R17, R18, R19, R20, R21, R22, R23, R24, R25, R26, R27, R28, R29, R30, R31, R32, R33, R34 | 34 | 100k | Resistor | https://eu.mouser.com/ProductDetail/Vishay-Beyschlag/MBA02040C1003FRP00?qs=mzRxyRlhVdt9crF7Zyf%2F5Q%3D%3D |  | 0.10 € | 3.40 € | 3.40 €
U1, U2 | 2 | MCP23017_SP | 16-bit I/O expander, I2C, interrupts, w pull-ups, SPDIP-28 | https://eu.mouser.com/ProductDetail/Microchip-Technology/MCP23017-E-SP?qs=usxtMOJb1RyESXZDw7ia5A%3D%3D |  | 1.53 € | 3.06 € | 3.06 €
 | 2 | Jumpers 2 pins |  | https://eu.mouser.com/ProductDetail/TE-Connectivity/1-881545-2?qs=G55MHhPmvtILJr8pg2%2FD4w%3D%3D |  | 0.30 € | 0.60 € | 0.60 €
 | 2 | 2.54mm Pitch Vertical 28 Way, Through Hole Turned Pin IC Dip Socket, 3A |  | https://befr.rs-online.com/web/p/dil-sockets/1831575 |  | 0.75 € | 1.50 € | 1.50 €
 |  |  |  |  |  |  | 91.27 € | 71.51 €

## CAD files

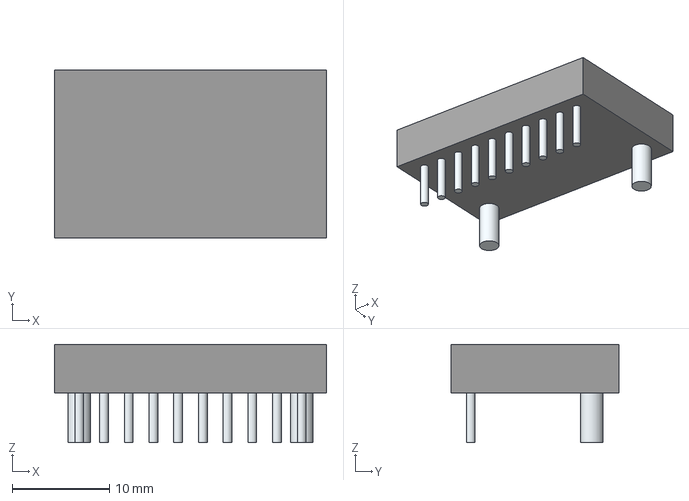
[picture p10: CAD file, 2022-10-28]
PCB_boards/measurement_boards/mb.2024.1.1/1085/3D/1085.stp
27.9 x 17.3 x 10.1 mm
Leads x 12

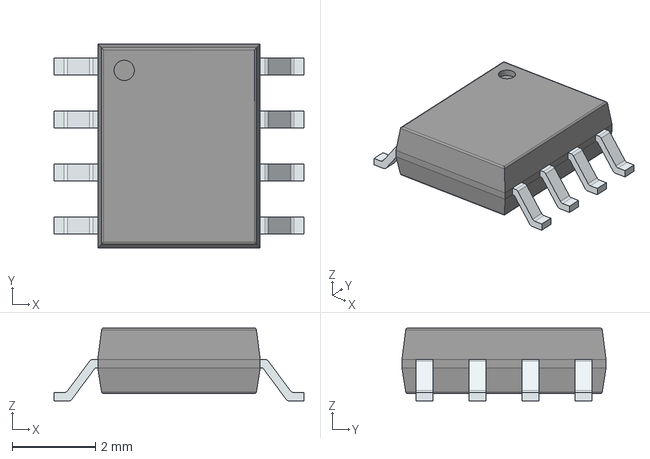
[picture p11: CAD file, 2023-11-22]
PCB_boards/measurement_boards/mb.2024.1.1/LIB_OP07CSZ-REEL/OP07CSZ-REEL.stp
6.00 x 4.90 x 1.75 mm
PinsArrayLR

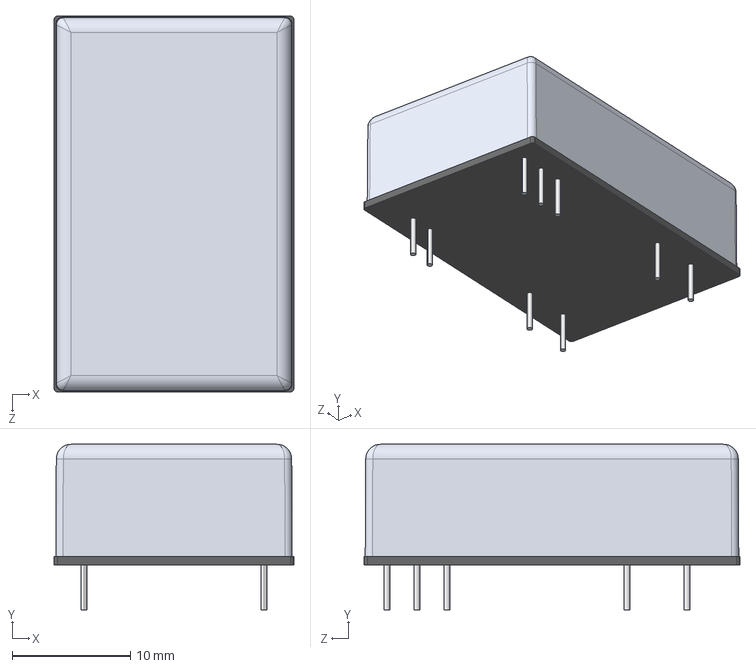
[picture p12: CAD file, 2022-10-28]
PCB_boards/measurement_boards/mb.2024.1.1/THD_15-1222N/THD_15-1222N.step
20.3 x 14.0 x 31.8 mm

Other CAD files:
PCB_boards/measurement_boards/mb.2024.1.1/1085/3D/1085.stl

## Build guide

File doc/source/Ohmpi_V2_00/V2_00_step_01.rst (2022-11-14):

**STEP n°1** : Raspberry Pi  configuration 
*******************************************

.. warning::
	**Ohmpi is a participative project open to all, it requires skills in electronics and to respect the safety rules. Ohmpi must be assembled in a professional context and by people competent in electronics. The Ohmpi team cannot be held responsible for any material or human damage which would be associated with the use or the assembly of OHMPI. The Ohmpi team cannot be held responsible if the equipment does not work after assembly.**

**PART A:** OS installation  
=============================

+----------------------------------------------------+---------------+
| **Required components**                            | **Quantity**  | 
+----------------------------------------------------+---------------+
|Raspberry Pi 4 Model B                              |              1|
+----------------------------------------------------+---------------+
|Micro SD 32 Go                                      |              1|
+----------------------------------------------------+---------------+
|HDMI Cable                                          |              1|
+----------------------------------------------------+---------------+
|Computer mouse                                      |              1|
+----------------------------------------------------+---------------+
|Computer Keyboard                                   |              1|
+----------------------------------------------------+---------------+

The first step is to start up the Raspberry Pi board, including installation of an OS (operating system). 
For this step, the installation instructions are well described on the Raspberry website 

1. Watch the vidéo `how to set up your raspberry Pi <https://www.youtube.com/watch?v=wjWZhV1v3Pk>`_.

2. The authors recommend installing the latest stable and complete version of Raspberry Pi OS (Previously called Raspbian) by using Raspberry Pi Imager.

3. or you can visit this `website <https://projects.raspberrypi.org/en/projects/raspberry-pi-setting-up>`.  

.. note:: 
	 All the development tests were performed on Raspberry Pi 3 Model B, we used the following version of Raspbian:
	 
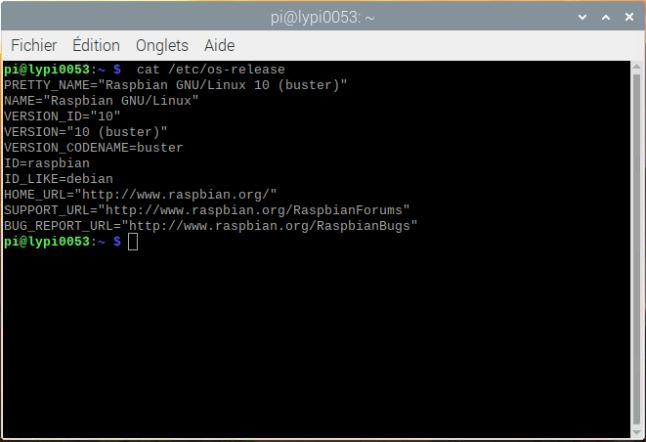
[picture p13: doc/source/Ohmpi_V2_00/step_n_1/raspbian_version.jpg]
	 

.. warning::
	 Once the OS has been installed,  **1-wire, spi and GPIO remote option** must be deactivated and **I2C option** must be activated via the Raspbian GUI settings menu. Failure to carry out this task may cause damage to the relay shield cards during measurements.

**PART B:** Virtual Environnement and packages
===============================================

A virtual environment is a way to have multiple, parallel instances of the Python interpreter, each with different package sets and different configurations. 
Each virtual environment contains a discrete copy of the Python interpreter, including copies of its support utilities. It also protects your system in case of problems with the packages.

All dependencies are specified in requirements.txt

.. note:: 
	 All instructions below should be typed in the terminal

It is first necessary to ensure that the libatlas-base-dev library is installed:

.. code-block:: python
	
	 sudo apt-get install libatlas-base-dev

We strongly recommend users to create a virtual environment to run the code and installed all required dependencies. It can be done either in a directory gathering all virtual environments used on the computer or within the ohmpy directory.

Create the virtual environment:

.. code-block:: python
	 
	 python3 -m venv ohmpy

Activate it using the following command:

.. code-block:: python
	 
	 source ohmpy/bin/activate

Install packages within the virtual environment. Installing the following package should be sufficient to meet dependencies:

.. code-block:: python
     
     export CFLAGS=-fcommon
	 sudo pip install RPi.GPIO adafruit-blinka numpy pandas adafruit-circuitpython-ads1x15 adafruit-circuitpython-tca9548a adafruit-circuitpython-mcp230xx gpiozero

Check that requirements are met using 

.. code-block:: python
	 
	 pip list

You should run you code within the virtual environment
to leave the virtual environment simply type:

.. code-block:: python
	  
	 deactivate

**PART C:** Activate virtual environnement on Thonny (Python IDE)  (on Rapberry Pi) 
====================================================================================

If you decided to use a virtual environment, it is necessary to setup Thonny Python IDE the first time you use it.

1- Run the Thonny Python IDE software, Click on raspebrry acces **menu > programming> Thonny pythonIDE**

2- Thonny's interface opens, Python runs on the Root (Python 3.7.3 (/usr/bin/python3))

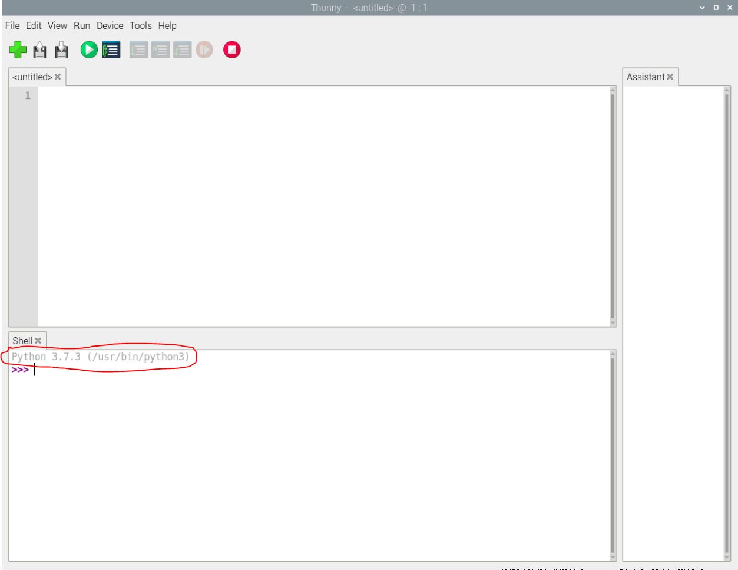
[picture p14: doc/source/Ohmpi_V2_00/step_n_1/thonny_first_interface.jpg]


3-Click on **Run>select interpreter**, a new window opens click on interpret

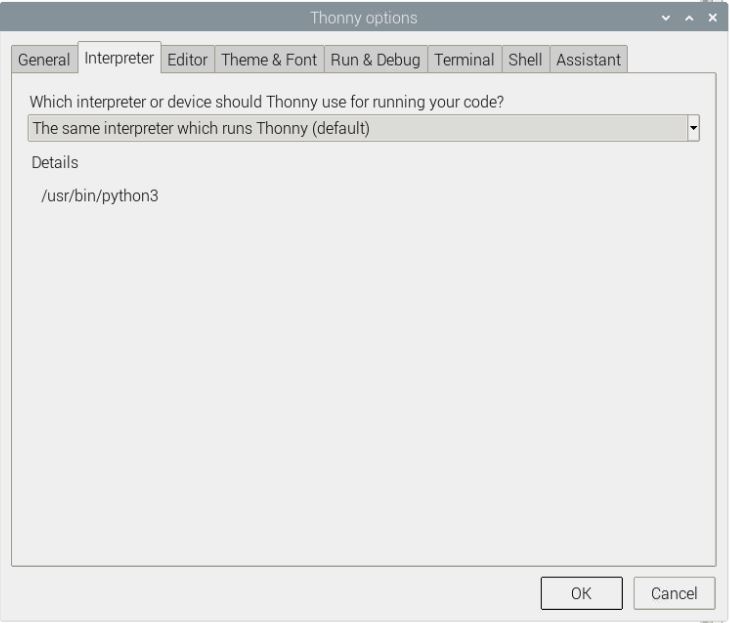
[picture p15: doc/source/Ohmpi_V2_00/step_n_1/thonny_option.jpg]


4-On the new open windows select **alternative Pyhton3 or virtual environnement**

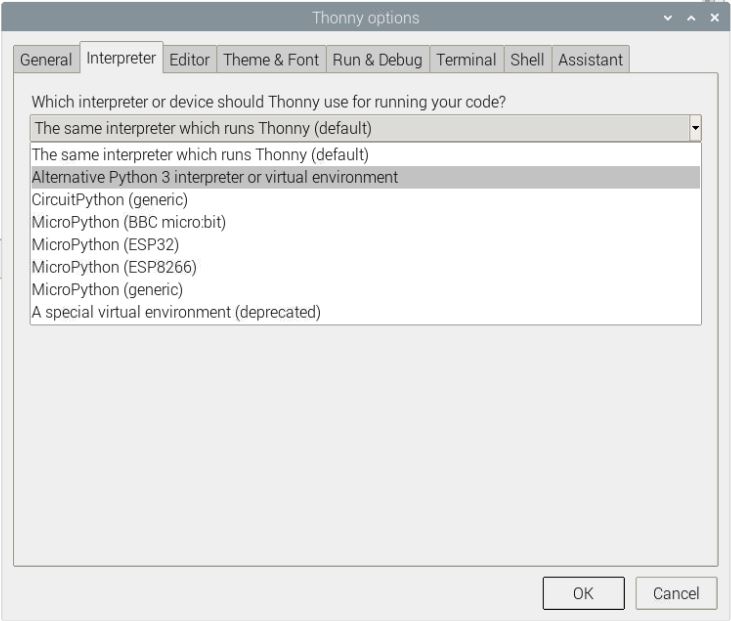
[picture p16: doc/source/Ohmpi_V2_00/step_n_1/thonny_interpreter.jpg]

	   
5- New buttons appeared, selected **"locate another python executable "**

6- A new window opens, find the folder where there is the python 3 file in the virtual environment folder previously created **/home/pi/ohmpi/bin/python3**.

7- In the **known interpreter** tab the path of the virtual environnementshould appear

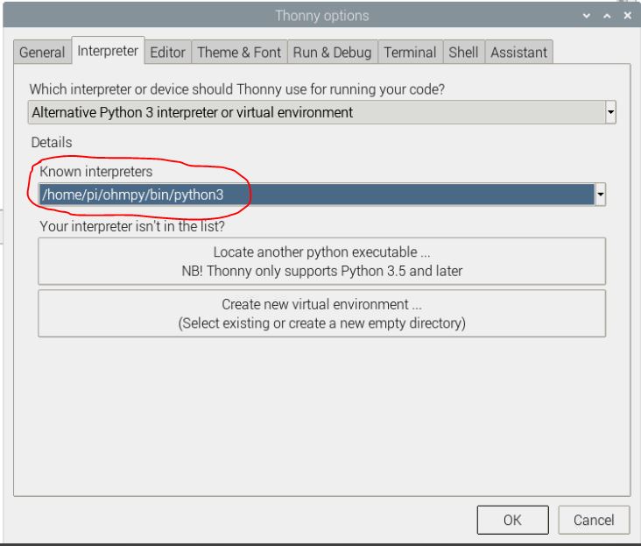
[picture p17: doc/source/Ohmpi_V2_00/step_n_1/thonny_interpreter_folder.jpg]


8- Close the window by clicking on **ok**.

9- Close thonny to save modifications

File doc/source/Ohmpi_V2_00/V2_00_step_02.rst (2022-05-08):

**STEP n°2**: Measurement board
****************************************************

.. warning::
	**Ohmpi is a participative project open to all, it requires skills in electronics and to respect the safety rules. Ohmpi must be assembled in a professional context and by people competent in electronics. The Ohmpi team cannot be held responsible for any material or human damage which would be associated with the use or the assembly of OHMPI. The Ohmpi team cannot be held responsible if the equipment does not work after assembly.**

**PART A** Assembly of measurement board
======================================================

Required components 
----------------------------------------------------

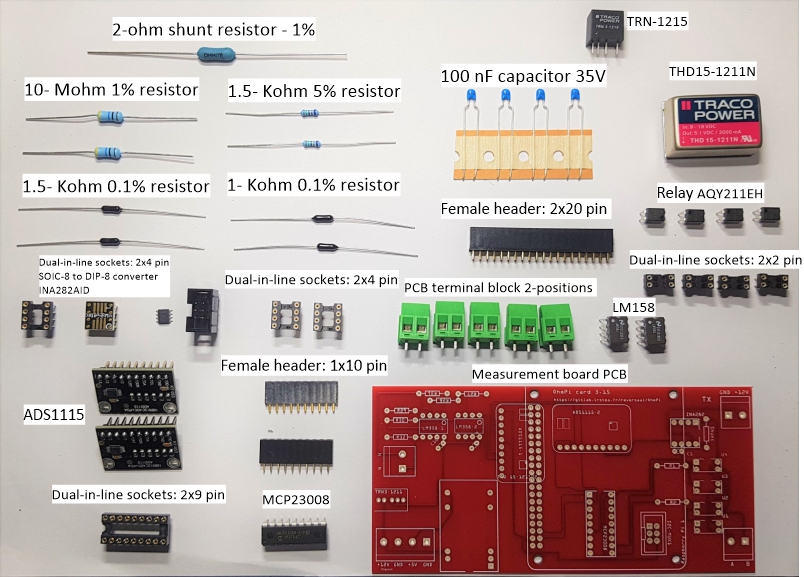
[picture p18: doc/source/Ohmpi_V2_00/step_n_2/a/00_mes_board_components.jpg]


.. csv-table:: List of components
   :file: step_n_2/a/Mesure_board_list_2_xx.csv
   :widths: 30, 70, 70, 70, 70, 35, 35
   :header-rows: 1
   
Description
------------------  

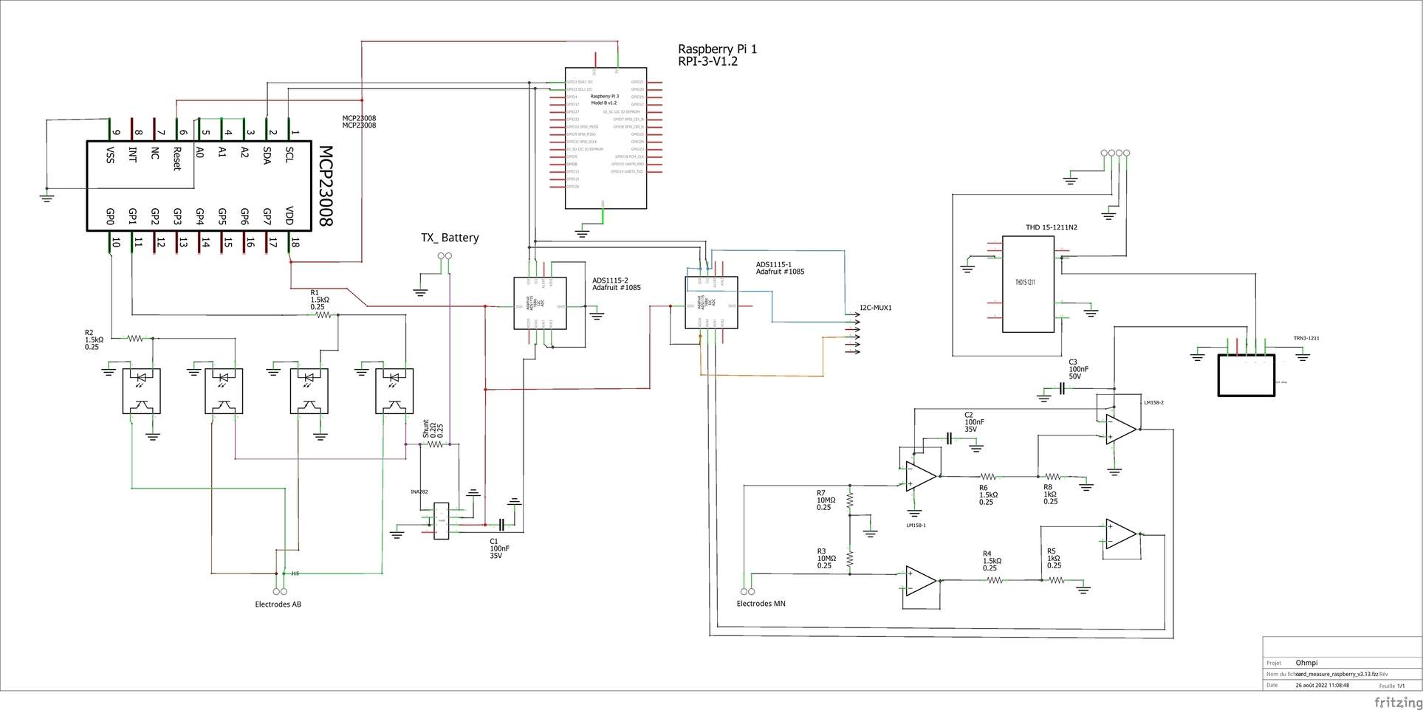
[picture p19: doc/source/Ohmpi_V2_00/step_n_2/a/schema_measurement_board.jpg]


Figure  shows the general schematics for the electronic measurement board developed.
We have developed a complete "plug and play" measurement board. To measure electrical resistivity with Raspberry Pi. 
two ADS1115 were used,one for the voltage measurement one for the current measurement, as proposed by Florsch [7]. The ADS1115
is a 16-bit ADC (Analog-to-Digital Converter), with an adaptable gain. The advantage of ADS1115 is that the 
input signal value could lie between - to + 6.114 V. For the current measurement we have directly integrated the INA282 component, 
which allows to realize precise current measurement around a shunt resistor. The assembly are described in the following steps:

.. table::
   :align: center
   
   +--------+------------------------------------------------------------+
   |        |   
   |      1 +------------------------------------------------------------+
   |        | Installation of female header, 1 by10  pins, for ADS1115   | 
   |        |                                                            |                                                                       
   +--------+------------------------------------------------------------+
   
.. table::
   :align: center
  
   +--------+------------------------------------------------------------+
   |        |   
   |2       +------------------------------------------------------------+
   |        | Soldering of 4 dual-in-line socket (2 by 2 pins) for       | 
   |        | optical relay, AQY211EH.                                   |                                                                       
   +--------+------------------------------------------------------------+
   
.. table::
   :align: center
  
   +--------+------------------------------------------------------------+
   |        |   
   |3       +------------------------------------------------------------+
   |        | Soldering of 1 dual-in-line socket (2 by 9 pins)           | 
   |        | for MCP23008.                                              |                                                                       
   +--------+------------------------------------------------------------+
   
.. table::
   :align: center
  
   +--------+------------------------------------------------------------+
   |        |   
   | 4      +------------------------------------------------------------+
   |        | Soldering of 1 dual-in-line socket (2 by 4 pins)           | 
   |        |                                                            |                                                                       
   +--------+------------------------------------------------------------+ 
.. table::
   :align: center
  
   +--------+------------------------------------------------------------+
   |        |   
   |5       +------------------------------------------------------------+
   |        | Soldering of 2 dual-in-line socket (2 by 4 pins)           | 
   |        |                                                            |                                                                       
   +--------+------------------------------------------------------------+
   
.. table::
   :align: center
  
   +--------+------------------------------------------------------------+
   |        |   
   | 6      +------------------------------------------------------------+
   |        | Traco Power Supply 12V to 5V, TDH15 - 1211N                | 
   |        |                                                            |                                                                       
   +--------+------------------------------------------------------------+  

.. table::
   :align: center
  
   +--------+------------------------------------------------------------+
   |        |   
   |7       +------------------------------------------------------------+
   |        | Four screw terminals for 12V inpout et 5V outpout          | 
   |        |                                                            |                                                                       
   +--------+------------------------------------------------------------+
   
.. table::
   :align: center
  
   +--------+------------------------------------------------------------+
   |        |   
   |8       +------------------------------------------------------------+
   |        | Traco power Supply 12V to 24V, TRN-1215                    | 
   |        |                                                            |                                                                       
   +--------+------------------------------------------------------------+    

.. table::
   :align: center
  
   +--------+------------------------------------------------------------+
   |        |   
   |9       +------------------------------------------------------------+
   |        | Two screw terminals electrodes M and N                     | 
   |        |                                                            |                                                                       
   +--------+------------------------------------------------------------+
   
.. table::
   :align: center
  
   +---------+------------------------------------------------------------+
   |         |   
   |10       +------------------------------------------------------------+
   |         | Four screw terminals, for 12V power supply and for         | 
   |         | electrodes A and B                                         |                                                                       
   +---------+------------------------------------------------------------+

.. table::
   :align: center
  
   +---------+------------------------------------------------------------+
   |         |   
   |11       +------------------------------------------------------------+
   |         |  Soldering three capacitors (100nF)                        | 
   |         |                                                            |                                                                       
   +---------+------------------------------------------------------------+

.. warning::
	 
	 In this version, We used a shunt resistor of 2 ohms, which limits the current measurement to 48 mA. If the current is higher than this value, you just have to decrease the value of the shunt resistor.Change the shunt value in the code.

.. table::
   :align: center
  
   +---------+------------------------------------------------------------+
   |         |   
   | 12      +------------------------------------------------------------+
   |         | 2 ohms shunt resistor pre-adjustment                       | 
   |         |                                                            |                                                                       
   +---------+------------------------------------------------------------+
.. table::
   :align: center
  
   +---------+------------------------------------------------------------+
   |         |   
   |13       +------------------------------------------------------------+
   |         | Soldering 2 ohms shunt resistor                            | 
   |         |                                                            |                                                                       
   +---------+------------------------------------------------------------+
   
.. table::
   :align: center
  
   +---------+------------------------------------------------------------+
   |         |   
   |14       +------------------------------------------------------------+
   |         | 1 Mohms resistors                                          | 
   |         |                                                            |                                                                       
   +---------+------------------------------------------------------------+  
   
.. table::
   :align: center
  
   +---------+------------------------------------------------------------+
   |         |   
   |15       +------------------------------------------------------------+
   |         | Soldering tow 1 Kohms resistors                            | 
   |         |                                                            |                                                                       
   +---------+------------------------------------------------------------+
   
.. table::
   :align: center
  
   +---------+------------------------------------------------------------+
   |         |   
   |16       +------------------------------------------------------------+
   |         | Soldering tow 1.5Kohms resistors                           | 
   |         |                                                            |                                                                       
   +---------+------------------------------------------------------------+
.. table::
   :align: center
  
   +---------+------------------------------------------------------------+
   |         |   
   |17       +------------------------------------------------------------+
   |         | Soldering tow 1.5Kohms resistors                           | 
   |         |                                                            |                                                                       
   +---------+------------------------------------------------------------+
   
.. table::
   :align: center
  
   +---------+------------------------------------------------------------+
   |         |   
   |18       +------------------------------------------------------------+
   |         | Female header 2 by 20 pins for Raspberry Pi connection     | 
   |         |                                                            |                                                                       
   +---------+------------------------------------------------------------+

.. table::
   :align: center
  
   +---------+------------------------------------------------------------+
   |         |   
   |19       +------------------------------------------------------------+
   |         | View of the female  header 2 by 20 pins installation       | 
   |         | for Raspberry Pi connection                                |                                                                       
   +---------+------------------------------------------------------------+
   
.. table::
   :align: center
  
   +---------+------------------------------------------------------------+
   |         |   
   |20       +------------------------------------------------------------+
   |         | Fixing MCP23008 component (Dot mark on the top left corner)| 
   |         |                                                            |                                                                       
   +---------+------------------------------------------------------------+
   
.. table::
   :align: center
  
   +---------+------------------------------------------------------------+
   |         |   
   |21       +------------------------------------------------------------+
   |         |Mounting optical relay, AQY211EH (Dot mark in the top left  | 
   |         |corners)                                                    |                                                                       
   +---------+------------------------------------------------------------+
   
.. table::
   :align: center
  
   +---------+------------------------------------------------------------+
   |         |   
   |22       +------------------------------------------------------------+
   |         | Mounting LM158 operational amplificator                    | 
   |         |                                                            |                                                                       
   +---------+------------------------------------------------------------+

.. table::
   :align: center
  
   +---------+------------------------------------------------------------+
   |         |   
   |23       +------------------------------------------------------------+
   |         |  Mounting ADS115 board                                     | 
   |         |                                                            |                                                                       
   +---------+------------------------------------------------------------+
   
.. table::
   :align: center
  
   +---------+------------------------------------------------------------+
   |         |   
   |24       +------------------------------------------------------------+
   |         | Fixing the INA282 (Dot mark in the top right corner)       | 
   |         |                                                            |                                                                       
   +---------+------------------------------------------------------------+

**PART B** Start-up of the measurement board
====================================================== 

+------------------------------------------------------------------------+
| **Required components**                                                | 
+------------------------------------------------------------------------+

.. csv-table:: List of components
   :file: step_n_2/b/test_2_xx.csv
   :widths: 30, 70, 70, 70, 70, 35, 35
   :header-rows: 1

.. table::
   :align: center
   
   +--------+------------------------------------------------------------+
   |        |   
   |1       +------------------------------------------------------------+
   |        | Shutdown the raspberry Pi and unplug the power supply      | 
   |        |                                                            |                                                                       
   +--------+------------------------------------------------------------+
   
.. table::
   :align: center
   
   +--------+--------------------------------------------------------------------------+
   |        |   
   |2       +--------------------------------------------------------------------------+
   |        | Mounting the bottom spacers on the Raspberry Pi (male/female, 11mm, M3)  | 
   |        |                                                                          |                                                                       
   +--------+--------------------------------------------------------------------------+

.. table::
   :align: center
   
   +--------+--------------------------------------------------------------------------+
   |        |   
   |3       +--------------------------------------------------------------------------+
   |        | Mounting the upper spacers on the Raspberry Pi (female/female, 11mm, M3) | 
   |        |                                                                          |                                                                       
   +--------+--------------------------------------------------------------------------+

.. table::
   :align: center
   
   +--------+------------------------------------------------------------+
   |        |   
   |4       +------------------------------------------------------------+
   |        | Mounting the Ohmpi's measurement board on the Raspberry Pi | 
   |        |                                                            |                                                                       
   +--------+------------------------------------------------------------+

.. table::
   :align: center
   
   +--------+------------------------------------------------------------+
   |        |   
   |5       +------------------------------------------------------------+
   |        | Mounting the Ohmpi's measurement board on the Raspberry Pi | 
   |        |                                                            |
   +--------+------------------------------------------------------------+   

.. table::
   :align: center
   
   +--------+------------------------------------------------------------+
   |        |   
   |6       +------------------------------------------------------------+
   |        | Plug the power supply into a socket and connect it to your | 
   |        | Raspberry Pi's power port.                                 |
   +--------+------------------------------------------------------------+  

**PART C** Check the measurement board
====================================================== 

 Run the terminal, and write

 .. code-block:: python

	 i2cdetect -y 1

.. table::
   :align: center
   
   +--------+------------------------------------------------------------+
   |        |   
   |1       +------------------------------------------------------------+
   |        |If everything is working, three I2C addresses should appear | 
   |        |on the screen.                                              |                                                                       
   +--------+------------------------------------------------------------+

Setting up an equivalent electronic circuit, for this you will need: 
 * 4 1kohm resistor (R2)
 * 1 220 ohm resistor (R1)
 * 1 small padboard
 * Spool of solder
 
 .. table::
   :align: left
 
   +--------+------------------------------------------------------------+
   |        |   
   |2       +------------------------------------------------------------+
   |        | Schematic of equivalent electronic circuit test            |                                                                       
   +--------+------------------------------------------------------------+
   
.. table::
   :align: center
 
   +--------+------------------------------------------------------------+
   |        |   
   |3       +------------------------------------------------------------+
   |        | Prepare the equivalent electronic circuit test             |                                                                       
   +--------+------------------------------------------------------------+ 

.. table::
   :align: center
 
   +--------+------------------------------------------------------------+
   |        |   
   |4       +------------------------------------------------------------+
   |        |  Prepare the battery connections and the terminals.        |                                                                       
   +--------+------------------------------------------------------------+ 

.. table::
   :align: center
 
   +--------+------------------------------------------------------------+
   |        |   
   |5       +------------------------------------------------------------+
   |        | Soldering cables and terminals                             |                                                                       
   +--------+------------------------------------------------------------+ 

.. table::
   :align: center
 
   +--------+------------------------------------------------------------+
   |        |   
   |6       +------------------------------------------------------------+
   |        |Install the red cables on the +12V terminal and black cable |                                                                       
   |        |on the ground terminal. Connect to two different 12V        |
   |        |batteries                                                   |
   +--------+------------------------------------------------------------+ 

.. table::
   :align: center
 
   +--------+------------------------------------------------------------+
   |        |   
   |7       +------------------------------------------------------------+
   |        | Connect the equivalent electronic circuit test             |                                                                       
   |        |                                                            |
   +--------+------------------------------------------------------------+

.. table::
   :align: center
 
   +--------+------------------------------------------------------------+
   |        |   
   |7       +------------------------------------------------------------+
   |        | Run Tonny Interpreter                                      |                    
   |        |                                                            |
   +--------+------------------------------------------------------------+   

.. table::
   :align: center
 
   +--------+------------------------------------------------------------+
   |        |   
   |7       +------------------------------------------------------------+
   |        | Run Ohmpi_4elec.py, if everything works you should         |                    
   |        | get the following result (220 ohm)                         |
   +--------+------------------------------------------------------------+

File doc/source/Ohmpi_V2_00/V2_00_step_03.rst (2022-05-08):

.. warning::
	**Ohmpi is a participative project open to all, it requires skills in electronics and to respect the safety rules. Ohmpi must be assembled in a professional context and by people competent in electronics. The Ohmpi team cannot be held responsible for any material or human damage which would be associated with the use or the assembly of OHMPI. The Ohmpi team cannot be held responsible if the equipment does not work after assembly.**

**STEP n°3:** MUX board
****************************************************
The multiplexing of the channels is a mechanical multiplexing based on OMRON's manufacturing relays (G5LE-1-VD 12 VDC). Each relay is combined with 
a ZVN4206A power MOFSET. The raspberry has only 30 GPIOs, which is not enough to activate all the 64 electrodes, which represent 512 GPIOs. 
We used gpio expender I2C (MCP23017). We have associated these components with an I2C muliplexer of type type TCA9548A from adafruit. 
This combination allows to go up to 512 GPIOs and up to 128 electrodes. Each card has its own digital address between 0X70 and 0X77. 
In the following presentation for an Ohmpi 64 electrodes, we will use the addresses 0X70 for channel A, 0X71 for channel B, 0X72 for channel M and 0X73 for channel N. 
0X73 for the N channel. 4 MUX board will be needed to multiplex an Ohmpi 64 electrodes.

**PART A** Assembly of MUX board
======================================================

Required components 
----------------------------------------------------

alternate text

.. csv-table:: List of components
   :file: step_n_3/a/MUX_board_list_2_xx.csv
   :widths: 30, 70, 70, 70, 70, 35, 35
   :header-rows: 1 

.. table::
   :align: center
   
   +--------+------------------------------------------------------------+
   |        |   
   |      1 +------------------------------------------------------------+
   |        |Mux board pcb                                               | 
   |        |                                                            |                                                                       
   +--------+------------------------------------------------------------+

.. table::
   :align: center
   
   +--------+------------------------------------------------------------+
   |        |   
   |      2 +------------------------------------------------------------+
   |        |Installation of the 100 Kohm resistors                      | 
   |        |                                                            |                                                                       
   +--------+------------------------------------------------------------+   
   
.. table::
   :align: center
   
   +--------+------------------------------------------------------------+
   |        |   
   |      3 +------------------------------------------------------------+
   |        |Installation of the mosfet ZVN4206A                         | 
   |        |                                                            |                                                                       
   +--------+------------------------------------------------------------+      

.. table::
   :align: center
   
   +--------+------------------------------------------------------------+
   |        |   
   |      4 +------------------------------------------------------------+
   |        |Installation of the diode-1n4007                            | 
   |        |                                                            |                                                                       
   +--------+------------------------------------------------------------+    
   
.. table::
   :align: center
   
   +--------+------------------------------------------------------------+
   |        |   
   |      5 +------------------------------------------------------------+
   |        |Installation of the relay                                   | 
   |        |                                                            |                                                                       
   +--------+------------------------------------------------------------+  

.. table::
   :align: center
   
   +--------+------------------------------------------------------------+
   |        |   
   |      6 +------------------------------------------------------------+
   |        |Installation of the terminal screw                          | 
   |        |                                                            |                                                                       
   +--------+------------------------------------------------------------+

.. table::
   :align: center
   
   +--------+------------------------------------------------------------+
   |        |   
   |      7 +------------------------------------------------------------+
   |        |Installation of generic male header                         | 
   |        |                                                            |                                                                       
   +--------+------------------------------------------------------------+ 

.. table::
   :align: center
   
   +--------+------------------------------------------------------------+
   |        |   
   |      8 +------------------------------------------------------------+
   |        |Installation of Pin strip (6 pins)  and pin strip (16 pins) | 
   |        |                                                            |                                                                       
   +--------+------------------------------------------------------------+  

.. table::
   :align: center
   
   +--------+------------------------------------------------------------+
   |        |   
   |      9 +------------------------------------------------------------+
   |        |Installation of DIP Dual In Line Socket 2*14                | 
   |        |                                                            |                                                                       
   +--------+------------------------------------------------------------+  

.. table::
   :align: center
   
   +--------+------------------------------------------------------------+
   |        |   
   |     10 +------------------------------------------------------------+
   |        |Installation of Adafruit TCA9548A                           | 
   |        |                                                            |                                                                       
   +--------+------------------------------------------------------------+

.. table::
   :align: center
   
   +--------+------------------------------------------------------------+
   |        |   
   |     10 +------------------------------------------------------------+
   |        |Installation of MCP23017                                    | 
   |        |                                                            |                                                                       
   +--------+------------------------------------------------------------+  
   
.. note:: 
	 This step must be duplicated 4 times for every Mux card.   

**PART B** MUX board address
====================================================== 
To build an ohmpi it is necessary to have 4 MUX boards, with 4 different addresses. It is therefore necessary to identify each board, by assigning an address, which will be allocated in the Ohmpi code.
We present here the addresses selected by default.

For the A electrode board, we suggest addressing it with address 0x70:

.. table::
   :align: center
   
   +--------+------------------------------------------------------------+
   |        |   
   |     1  +------------------------------------------------------------+
   |        |Mount the jumpers and note the value of the address and the |
   |        |electrode name on the mux board (A).                        |                                                                       
   |        +------------------------------------------------------------+  
   |        |   
   |        +------------------------------------------------------------+
   |        |Zoom on the jumper                                          | 
   |        |                                                            |   
   +--------+------------------------------------------------------------+   

For the B electrode board, we suggest addressing it with address 0x71:

.. table::
   :align: center
   
   +--------+------------------------------------------------------------+
   |        |   
   |     2  +------------------------------------------------------------+
   |        |Mount the jumpers and note the value of the address and the |
   |        |electrode name on the mux board (B).                        |                                                                       
   |        +------------------------------------------------------------+  
   |        |   
   |        +------------------------------------------------------------+
   |        |Zoom on the jumper                                          | 
   |        |                                                            |   
   +--------+------------------------------------------------------------+ 

For the N electrode board, we suggest addressing it with address 0x72:

.. table::
   :align: center
   
   +--------+------------------------------------------------------------+
   |        |   
   |     3  +------------------------------------------------------------+
   |        |Mount the jumpers and note the value of the address and the |
   |        |electrode name on the mux board (B).                        |                                                                     
   |        +------------------------------------------------------------+  
   |        |   
   |        +------------------------------------------------------------+
   |        |Zoom on the jumper                                          | 
   |        |                                                            |   
   +--------+------------------------------------------------------------+ 

For the M electrode board, we suggest addressing it with address 0x73: 
  
.. table::
   :align: center
   
   +--------+------------------------------------------------------------+
   |        |   
   |     4  +------------------------------------------------------------+
   |        |Mount the jumpers and note the value of the address and the |
   |        |electrode name on the mux board (B).                        |                                                                     
   |        +------------------------------------------------------------+  
   |        |   
   |        +------------------------------------------------------------+
   |        |Zoom on the jumper                                          | 
   |        |                                                            |   
   +--------+------------------------------------------------------------+    

**PART C** Validation of MUX board
======================================================
The first step is to test the Mux boards before assembling them definitively.
To test the Mux boards, it will be necessary first to make a simplified assembly of the Mux board and the measurement board.

The first thing to do is to prepare a 50 cm long flat wire with two 6-poles connectors.

   +--------+------------------------------------------------------------+
   |        |   
   |     1  +------------------------------------------------------------+
   |        |Build a cable with 6 contacts with 6 pins connector.        |
   |        |                                                            |                                                                     
   +--------+------------------------------------------------------------+ 
 
   +--------+------------------------------------------------------------+
   |        |   
   |     2  +------------------------------------------------------------+
   |        |Prepare the measurement board and the first mux board by    |
   |        |example the card with address 0x71.                         |                                                                     
   +--------+------------------------------------------------------------+

   +--------+------------------------------------------------------------+
   |        |   
   |     3  +------------------------------------------------------------+
   |        |Connect the cables for the 12V power supply to the MUX board|
   |        |without powering the board.                                 |                                                                     
   +--------+------------------------------------------------------------+   

   +--------+------------------------------------------------------------+
   |        |   
   |     4  +------------------------------------------------------------+
   |        |Connect the 12V power supply screw terminal of the mux board|
   |        |to the 12V screw terminal power supply of the measurement   |
   |        |board.                                                      |
   +--------+------------------------------------------------------------+   

   +--------+------------------------------------------------------------+
   |        |   
   |     5  +------------------------------------------------------------+
   |        |Connect the 6-contact cable                                 |
   |        |                                                            |                                                                     
   +--------+------------------------------------------------------------+

Start your 12V power supply, the raspberry must start. 

Run the terminal and write:

 .. code-block:: python

	 i2cdetect -y 1 

Three addresses should appear, including the address of the MUX board you have selected. This implies that your board has been detected.

Open the script called "test_mux_board.py".

Run the script

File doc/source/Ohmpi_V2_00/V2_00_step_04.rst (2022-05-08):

.. warning::
	**Ohmpi is a participative project open to all, it requires skills in electronics and to respect the safety rules. Ohmpi must be assembled in a professional context and by people competent in electronics. The Ohmpi team cannot be held responsible for any material or human damage which would be associated with the use or the assembly of OHMPI. The Ohmpi team cannot be held responsible if the equipment does not work after assembly.**

**STEP n°4:** assemble Ohmpi 
****************************************************
   
.. table::
   :align: center
   
   +--------+------------------------------------------------------------+
   |        |   
   |      1 +------------------------------------------------------------+
   |        |Cut 4 ribbon cables composed of 16 wires each to the proper | 
   |        |length (about 1.5m). Each wire corresponds to an electrode. |                                                                      
   +--------+------------------------------------------------------------+

.. table::
   :align: center

   +--------+------------------------------------------------------------+
   |        |   
   |      2 +------------------------------------------------------------+
   |        |Crimp the ribbon cable on the corresponding idc connector   | 
   |        |with a suitable clamp. Pay attention to the direction of the|                                                                      
   |        |cables. Unbalanced IDC connector. The ribbon cable must be  | 
   |        |perpendicular to the connector.                             |
   +--------+------------------------------------------------------------+
   
.. table::
   :align: center

   +--------+------------------------------------------------------------+
   |        |   
   |      3 +------------------------------------------------------------+
   |        |Example of IDC connector mounting. The wires should run as  | 
   |        |perpendicular as possible to the IDC connector.             |                                                                      
   +--------+------------------------------------------------------------+   

.. table::
   :align: center

   +--------+------------------------------------------------------------+
   |        |   
   |      4 +------------------------------------------------------------+
   |        |Same for a 6 wires ribbon cable of 1 m length.              | 
   |        |                                                            |                                                                      
   +--------+------------------------------------------------------------+  

.. table::
   :align: center

   +--------+------------------------------------------------------------+
   |        |   
   |      5 +------------------------------------------------------------+
   |        |Cut the ribbon cable flush with the IDC connector.          | 
   |        |                                                            |                                                                      
   +--------+------------------------------------------------------------+  

.. table::
   :align: center

   +--------+------------------------------------------------------------+
   |        |   
   |      6 +------------------------------------------------------------+
   |        |Position 9 spacers above the MUX board, and 9 spacers below.| 
   |        |                                                            |                                                                      
   +        +------------------------------------------------------------+
   |        |   
   |        +------------------------------------------------------------+
   |        |Profile view for mounting the spacers above and below.      | 
   |        |                                                            |                                                                      
   +--------+------------------------------------------------------------+ 

.. table::
   :align: center

   +--------+------------------------------------------------------------+
   |        |   
   |      7 +------------------------------------------------------------+
   |        |Cut a 50 cm long wire of any color (here yellow). Strip and | 
   |        |tin each end of the wire. Install the wire "A" on the screw |
   |        |terminal of MUX board « A ».                                |                                                                                       
   +--------+------------------------------------------------------------+

.. table::
   :align: center

   +--------+------------------------------------------------------------+
   |        |   
   |      8 +------------------------------------------------------------+
   |        |Cut a red wire and a black wire of 50 cm length. Strip, tin | 
   |        |and position the wires on the left screw terminal as shown  |
   |        |in the picture: i)Red wire 12 V, ii) Black wire GND         |                                                                                       
   +--------+------------------------------------------------------------+

.. table::
   :align: center

   +--------+------------------------------------------------------------+
   |        |   
   |      9 +------------------------------------------------------------+
   |        |Mount the 4 ribbon cables (16-wires each) with IDC          | 
   |        |connectors. A small noise is often heard when the IDC       |
   |        |connector is clipped in place.                              |                                                                                       
   +--------+------------------------------------------------------------+

.. table::
   :align: center

   +--------+------------------------------------------------------------+
   |        |   
   |      10+------------------------------------------------------------+
   |        |Mount the ribbon cables with 6-wires with the corresponding | 
   |        |IDC connectors                                              |
   |        |                                                            |                                                                                       
   +--------+------------------------------------------------------------+ 

.. table::
   :align: center

   +--------+------------------------------------------------------------+
   |        |   
   |      11+------------------------------------------------------------+
   |        |Cut a red wire and a black wire of 10 cm length. Strip and  | 
   |        |tin the wires at the ends. Mount the red wire on the 12V    |
   |        |input and the black wire on the GND input on the right screw|
   |        |terminal.                                                   |                            
   +--------+------------------------------------------------------------+ 

.. table::
   :align: center

   +--------+------------------------------------------------------------+
   |        |   
   |      12+------------------------------------------------------------+
   |        |Mount and fix the second MUX board "B" on the first with    | 
   |        |the help of 9 spacers.                                      |
   |        |                                                            |
   |        |                                                            |                            
   +--------+------------------------------------------------------------+   

.. table::
   :align: center

   +--------+------------------------------------------------------------+
   |        |   
   |      13+------------------------------------------------------------+
   |        |Cut, strip and tin a red wire and a black wire of 10 cm     | 
   |        |length. Mount the wires on the left screw terminal.         |
   |        |Red wire 12V input, black wire GND input.                   |
   |        |Connect the red and black wires from board A to the right   |                            
   |        |screw terminal of board B. Red wire 12V input. Black wire   |   
   |        |GND input.                                                  |
   +--------+------------------------------------------------------------+  

.. table::
   :align: center

   +--------+------------------------------------------------------------+
   |        |   
   |      14+------------------------------------------------------------+
   |        |Crimp a 16 wires IDC connector on the ribbon cable at about | 
   |        |15 cm from the previous connector. Please, pay attention to |
   |        |the direction of the cable before the crimp procedure.      |
   |        |Mount the ribbon cable on the IDC connector on the board.   |                            
   +--------+------------------------------------------------------------+  

.. table::
   :align: center

   +--------+------------------------------------------------------------+
   |        |   
   |      15+------------------------------------------------------------+
   |        |Repeat the operation for the other 3 ribbon cables.         |                  
   +--------+------------------------------------------------------------+ 

.. table::
   :align: center

   +--------+------------------------------------------------------------+
   |        |   
   |      16+------------------------------------------------------------+
   |        |Repeat the operation for the 6 wires ribbon cable.          |                  
   +--------+------------------------------------------------------------+ 

.. table::
   :align: center

   +--------+------------------------------------------------------------+
   |        |   
   |      17+------------------------------------------------------------+
   |        |Cut a 50 cm long wire "here purple" (Color not relevant but | 
   |        |to be defined). Strip and tin the wire at its ends. Position|
   |        |the wire on the input B of the screw terminal of the        |
   |        |multiplexing board B.                                       |                            
   +--------+------------------------------------------------------------+ 

.. table::
   :align: center

   +--------+------------------------------------------------------------+
   |        |   
   |      18+------------------------------------------------------------+
   |        |Repeat all these operations for the third MUX board         | 
   |        |called "M".                                                 |           
   +--------+------------------------------------------------------------+    

.. table::
   :align: center

   +--------+------------------------------------------------------------+
   |        |   
   |      19+------------------------------------------------------------+
   |        |Repeat the operations for the fourth MUX Boards. Attention, | 
   |        |it is necessary to position 5 different spacers (here nylon |
   |        |screw hex spacers) in between the “M” board and the “N” MUX |
   |        |Board (as shown on the photograph). Refer to the following  |                            
   |        |photographs for more details on the assembly of the spacers.|                                                 
   +--------+------------------------------------------------------------+

.. table::
   :align: center

   +--------+------------------------------------------------------------+
   |        |   
   |      20+------------------------------------------------------------+
   |        |When mounting the 4th MUX board ("N"), screws can be placed |
   |        |on the nylon spacers to fix the boards together. Note that  |
   |        |the other spacers could be used for this purpose.           |
   |        |Connect ribbon cables (16 wires) from board 3 to board 4 as |
   |        |previously described. Connect the red wire (12V) of MUX     |                                                 
   |        |board "M" to the 12V terminal of the right screw terminal   |   
   |        |of MUX Board "N". Connect the black wire (GND) of MUX board |
   |        |“M” to the GND screw terminal on MUX board “N”.             |  
   +--------+------------------------------------------------------------+   

.. table::
   :align: center

   +--------+------------------------------------------------------------+
   |        |   
   |      21+------------------------------------------------------------+
   |        |Cut a red wire and a black wire of one meter length. Place  | 
   |        |the red wire on terminal “12V” and the black wire on        |
   |        |terminal “GND” of the left screw terminal. Tie the wires    |
   |        |together.                                                   |                            
   +--------+------------------------------------------------------------+   

.. table::
   :align: center

   +--------+------------------------------------------------------------+
   |        |   
   |      22+------------------------------------------------------------+
   |        |Tie the A, B, M and N wires together                        |                            
   +--------+------------------------------------------------------------+   

.. table::
   :align: center

   +--------+------------------------------------------------------------+
   |        |   
   |      23+------------------------------------------------------------+
   |        |Cut a PVC plate with the following minimum dimensions :     |  
   |        |200 mm * 150 mm * 5 mm                                      |                       
   +--------+------------------------------------------------------------+ 

.. table::
   :align: center

   +--------+------------------------------------------------------------+
   |        |   
   |      24+------------------------------------------------------------+
   |        |Drill the plate to mount it on the remaining metal spacers. |  
   |        |Do not tighten the assembly.                                |                       
   +--------+------------------------------------------------------------+    
   
.. table::
   :align: center

   +--------+------------------------------------------------------------+
   |        |   
   |      25+------------------------------------------------------------+
   |        |Position the Raspberry Pi (RPI) board on the plate so that  |  
   |        |you can access the USB ports. Mark the holes of the RPI     |
   |        |board on the plate for mounting.                            |
   +--------+------------------------------------------------------------+

.. table::
   :align: center

   +--------+------------------------------------------------------------+
   |        |   
   |      26+------------------------------------------------------------+
   |        |Add spacers on the PVC plate.                               |     
   +--------+------------------------------------------------------------+ 

.. table::
   :align: center

   +--------+------------------------------------------------------------+
   |        |   
   |      27+------------------------------------------------------------+
   |        |Attach the PVC plate to the metal spacers with washers      |     
   |        |and nuts.                                                   |                                
   +--------+------------------------------------------------------------+  

.. table::
   :align: center

   +--------+------------------------------------------------------------+
   |        |   
   |      28+------------------------------------------------------------+
   |        |Position and fix the RPI card on the spacers                |     
   +--------+------------------------------------------------------------+     

.. table::
   :align: center

   +--------+------------------------------------------------------------+
   |        |   
   |      29+------------------------------------------------------------+
   |        |Add spacers on the RPI board. The red (12V) and black (GND) |     
   |        |wires coming out of the "M" MUX board must pass under       |    
   |        |the RPI board.                                              |        
   +--------+------------------------------------------------------------+ 

.. table::
   :align: center

   +--------+------------------------------------------------------------+
   |        |   
   |      30+------------------------------------------------------------+
   |        |Place the measurement board on the RPI GPIO outputs and on  |
   |        |the pre-positioned spacers. Note that LEDs are present on   |
   |        |this measurement board with an associated resistance simply |
   |        |for testing purposes (do not consider this temporary        |
   |        |modification of the board). Same for the orange wire present|                                                 
   |        |on the board.                                               |   
   +--------+------------------------------------------------------------+  

.. table::
   :align: center

   +--------+------------------------------------------------------------+
   |        |   
   |      31+------------------------------------------------------------+
   |        |Connect the wires " A " (here yellow), " B " (here purple), |
   |        |" M " (here brown) and " N " (here blue) on the             |
   |        |corresponding terminal blocks on the measurement board.     |
   |        |Connect the 6 wires ribbon cable on the measurement board   |
   |        |by passing under the PVC plate.Connect the red and black    |                                                 
   |        |wires to the 12 V and GND terminal block.                   |   
   +--------+------------------------------------------------------------+   

.. table::
   :align: center

   +--------+------------------------------------------------------------+
   |        |   
   |      32+------------------------------------------------------------+
   |        |Top view of the assembly. Add clips to secure the wires     |     
   |        |together.                                                   |
   +--------+------------------------------------------------------------+ 

.. table::
   :align: center

   +--------+------------------------------------------------------------+
   |        |   
   |      33+------------------------------------------------------------+
   |        |Second view.                                                |     
   +--------+------------------------------------------------------------+    

.. table::
   :align: center

   +--------+------------------------------------------------------------+
   |        |   
   |      34+------------------------------------------------------------+
   |        |Zoom in on the connection of the M and N wires.             |     
   +--------+------------------------------------------------------------+ 

.. table::
   :align: center

   +--------+------------------------------------------------------------+
   |        |   
   |      35+------------------------------------------------------------+
   |        |Zoom in on the connection of the A and B wires.             |     
   +--------+------------------------------------------------------------+ 

.. table::
   :align: center

   +--------+------------------------------------------------------------+
   |        |   
   |      36+------------------------------------------------------------+
   |        |Zoom in on the connection of the « 12V » and « GND » wires. |     
   +--------+------------------------------------------------------------+ 

.. table::
   :align: center

   +--------+------------------------------------------------------------+
   |        |   
   |      37+------------------------------------------------------------+
   |        |Fixing the measurement board on the spacers present on the  |
   |        |RPI board.                                                  |
   +--------+------------------------------------------------------------+
   
.. table::
   :align: center

   +--------+------------------------------------------------------------+
   |        |   
   |      38+------------------------------------------------------------+
   |        |Place the SD card containing the OS and the pre-installed   |
   |        |programs. Connect a mouse and a keyboard to the USB inputs  |
   |        |of the RPI board. Connect a monitor to the HDMI output of   |
   |        |the RPI board.                                              |                                                  
   +--------+------------------------------------------------------------+   

.. table::
   :align: center

   +--------+------------------------------------------------------------+
   |        |   
   |      39+------------------------------------------------------------+
   |        |Connect the red and black cables of board A to a 12V battery|
   |        |or other laboratory power supply delivering a 12V-DC        |
   |        |voltage.                                                    |
   |        |Enjoy 😊                                                    |                                                  
   +--------+------------------------------------------------------------+

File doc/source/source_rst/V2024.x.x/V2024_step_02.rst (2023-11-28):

**STEP n°2**: Measurement board
****************************************************

.. warning::
    **Ohmpi is a participative project open to all, it requires skills in electronics and to respect the safety rules. OhmPi must be assembled in a professional context and by people competent in electronics. The OhmPi team cannot be held responsible for any material or human damage which would be associated with the use or the assembly of OHMPI. The OhmPi team cannot be held responsible if the equipment does not work after assembly.**

**PART A** Assembly of the measurement board
======================================================

Required components 
----------------------------------------------------

alternate text

.. csv-table:: List of components
   :file: ../../img/v2023.x.x/step_n_2/a/measure_board_list_2_xx.csv
   :widths: 30, 70, 70, 70, 70, 35, 35
   :header-rows: 1
   
Description
------------------  

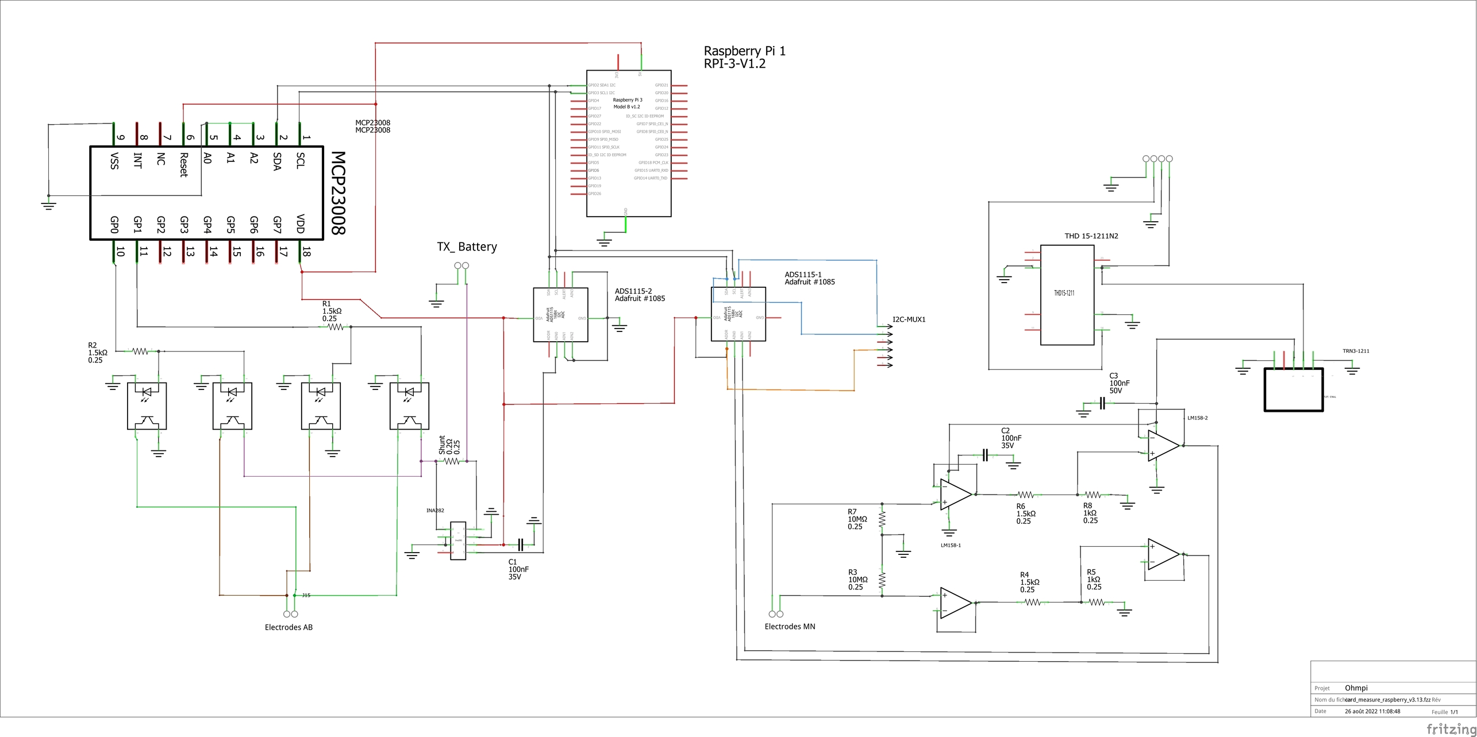
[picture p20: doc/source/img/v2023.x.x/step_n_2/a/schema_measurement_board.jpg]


Figure  shows the general schematics for the electronic measurement board developed.
We have developed a complete "plug and play" measurement board. To measure electrical resistivity with Raspberry Pi. 
two ADS1115 were used,one for the voltage measurement one for the current measurement, as proposed by Florsch [7]. The ADS1115
is a 16-bit ADC (Analog-to-Digital Converter), with an adaptable gain. The advantage of ADS1115 is that the 
input signal value could lie between - to + 6.114 V. For the current measurement we have directly integrated the INA282 component, 
which allows to realize precise current measurement around a shunt resistor. The assembly are described in the following steps:

.. table::
   :align: center
   
   +--------+-------------------------------------------------------------+
   |        |   
   |      1 +-------------------------------------------------------------+
   |        | Installation of female header, 1 by 10  pins, for ADS1115   | 
   |        |                                                             |                                                                       
   +--------+-------------------------------------------------------------+
   
.. table::
   :align: center
  
   +--------+-------------------------------------------------------------+
   |        |   
   |2       +-------------------------------------------------------------+
   |        | Soldering of 4 dual-in-line socket (2 by 2 pins) for        | 
   |        | optical relay, AQY211EH.                                    |                                                                       
   +--------+-------------------------------------------------------------+
   
.. table::
   :align: center
  
   +--------+------------------------------------------------------------+
   |        |   
   |3       +------------------------------------------------------------+
   |        | Soldering of 1 dual-in-line socket (2 by 9 pins)           | 
   |        | for MCP23008.                                              |                                                                       
   +--------+------------------------------------------------------------+
   
.. table::
   :align: center
  
   +--------+------------------------------------------------------------+
   |        |   
   | 4      +------------------------------------------------------------+
   |        | Soldering of 1 dual-in-line socket (2 by 4 pins)           | 
   |        |                                                            |                                                                       
   +--------+------------------------------------------------------------+ 
.. table::
   :align: center
  
   +--------+------------------------------------------------------------+
   |        |   
   |5       +------------------------------------------------------------+
   |        | Soldering of 2 dual-in-line socket (2 by 4 pins)           | 
   |        |                                                            |                                                                       
   +--------+------------------------------------------------------------+
   
.. table::
   :align: center
  
   +--------+------------------------------------------------------------+
   |        |   
   | 6      +------------------------------------------------------------+
   |        | Traco Power Supply 12V to 5V, TDH15 - 1211N                | 
   |        |                                                            |                                                                       
   +--------+------------------------------------------------------------+  

.. table::
   :align: center
  
   +--------+------------------------------------------------------------+
   |        |   
   |7       +------------------------------------------------------------+
   |        | Four screw terminals for 12V inpout et 5V output           |
   |        |                                                            |                                                                       
   +--------+------------------------------------------------------------+
   
.. table::
   :align: center
  
   +--------+------------------------------------------------------------+
   |        |   
   |8       +------------------------------------------------------------+
   |        | Traco power Supply 12V to 24V, TRN-1215                    | 
   |        |                                                            |                                                                       
   +--------+------------------------------------------------------------+    

.. table::
   :align: center
  
   +--------+------------------------------------------------------------+
   |        |   
   |9       +------------------------------------------------------------+
   |        | Two screw terminals electrodes M and N                     | 
   |        |                                                            |                                                                       
   +--------+------------------------------------------------------------+
   
.. table::
   :align: center
  
   +---------+------------------------------------------------------------+
   |         |   
   |10       +------------------------------------------------------------+
   |         | Four screw terminals, for 12V power supply and for         | 
   |         | electrodes A and B                                         |                                                                       
   +---------+------------------------------------------------------------+

.. table::
   :align: center
  
   +---------+------------------------------------------------------------+
   |         |   
   |11       +------------------------------------------------------------+
   |         |  Soldering three capacitors (100nF)                        | 
   |         |                                                            |                                                                       
   +---------+------------------------------------------------------------+

.. warning::
     
     In this version, we used a shunt resistor of 2 ohms, which limits the current measurement to 48 mA. If the current is higher than this value, you just have to decrease the value of the shunt resistor. Don't forget to change the shunt value in the config.py file (value associated to key 'R_shunt' in the OHMPI_CONFIG dict).

.. table::
   :align: center
  
   +---------+------------------------------------------------------------+
   |         |   
   | 12      +------------------------------------------------------------+
   |         | 2 ohms shunt resistor pre-adjustment                       | 
   |         |                                                            |                                                                       
   +---------+------------------------------------------------------------+
.. table::
   :align: center
  
   +---------+------------------------------------------------------------+
   |         |   
   |13       +------------------------------------------------------------+
   |         | Soldering 2 ohms shunt resistor                            | 
   |         |                                                            |                                                                       
   +---------+------------------------------------------------------------+
   
.. table::
   :align: center
  
   +---------+------------------------------------------------------------+
   |         |   
   |14       +------------------------------------------------------------+
   |         | 1 MOhm resistors                                           |
   |         |                                                            |                                                                       
   +---------+------------------------------------------------------------+  
   
.. table::
   :align: center
  
   +---------+------------------------------------------------------------+
   |         |   
   |15       +------------------------------------------------------------+
   |         | Soldering tow 1 kOhm resistors                             |
   |         |                                                            |                                                                       
   +---------+------------------------------------------------------------+
   
.. table::
   :align: center
  
   +---------+------------------------------------------------------------+
   |         |   
   |16       +------------------------------------------------------------+
   |         | Soldering two 1.5 kOhm resistors                           |
   |         |                                                            |                                                                       
   +---------+------------------------------------------------------------+
.. table::
   :align: center
  
   +---------+------------------------------------------------------------+
   |         |   
   |17       +------------------------------------------------------------+
   |         | Soldering two 1.5 kOhms resistors                          |
   |         |                                                            |                                                                       
   +---------+------------------------------------------------------------+
   
.. table::
   :align: center
  
   +---------+------------------------------------------------------------+
   |         |   
   |18       +------------------------------------------------------------+
   |         | Female header 2 by 20 pins for Raspberry Pi connection     | 
   |         |                                                            |                                                                       
   +---------+------------------------------------------------------------+

.. table::
   :align: center
  
   +---------+------------------------------------------------------------+
   |         |   
   |19       +------------------------------------------------------------+
   |         | View of the female  header 2 by 20 pins installation       | 
   |         | for Raspberry Pi connection                                |                                                                       
   +---------+------------------------------------------------------------+
   
.. table::
   :align: center
  
   +---------+------------------------------------------------------------+
   |         |   
   |20       +------------------------------------------------------------+
   |         | Fixing MCP23008 component (Dot mark on the top left corner)| 
   |         |                                                            |                                                                       
   +---------+------------------------------------------------------------+
   
.. table::
   :align: center
  
   +---------+------------------------------------------------------------+
   |         |   
   |21       +------------------------------------------------------------+
   |         |Mounting optical relay, AQY211EH (Dot mark in the top left  | 
   |         |corners)                                                    |                                                                       
   +---------+------------------------------------------------------------+
   
.. table::
   :align: center
  
   +---------+------------------------------------------------------------+
   |         |   
   |22       +------------------------------------------------------------+
   |         | Mounting LM158 operational amplifier                       |
   |         |                                                            |                                                                       
   +---------+------------------------------------------------------------+

.. table::
   :align: center
  
   +---------+------------------------------------------------------------+
   |         |   
   |23       +------------------------------------------------------------+
   |         |  Mounting ADS115 board                                     | 
   |         |                                                            |                                                                       
   +---------+------------------------------------------------------------+
   
.. table::
   :align: center
  
   +---------+------------------------------------------------------------+
   |         |   
   |24       +------------------------------------------------------------+
   |         | Fixing the INA282 (Dot mark in the top right corner)       | 
   |         |                                                            |                                                                       
   +---------+------------------------------------------------------------+

**PART B** Start-up of the measurement board
====================================================== 

+------------------------------------------------------------------------+
| **Required components**                                                | 
+------------------------------------------------------------------------+

.. csv-table:: List of components
   :file: ../../img/v2023.x.x/step_n_2/b/test_2_xx.csv
   :widths: 30, 70, 70, 70, 70, 35, 35
   :header-rows: 1

.. table::
   :align: center
   
   +--------+------------------------------------------------------------+
   |        |   
   |1       +------------------------------------------------------------+
   |        | Shutdown the raspberry Pi and unplug the power supply      | 
   |        |                                                            |                                                                       
   +--------+------------------------------------------------------------+
   
.. table::
   :align: center
   
   +--------+--------------------------------------------------------------------------+
   |        |   
   |2       +--------------------------------------------------------------------------+
   |        | Mounting the bottom spacers on the Raspberry Pi (male/female, 11mm, M3)  | 
   |        |                                                                          |                                                                       
   +--------+--------------------------------------------------------------------------+

.. table::
   :align: center
   
   +--------+--------------------------------------------------------------------------+
   |        |   
   |3       +--------------------------------------------------------------------------+
   |        | Mounting the upper spacers on the Raspberry Pi (female/female, 11mm, M3) | 
   |        |                                                                          |                                                                       
   +--------+--------------------------------------------------------------------------+

.. table::
   :align: center
   
   +--------+------------------------------------------------------------+
   |        |   
   |4       +------------------------------------------------------------+
   |        | Mounting the OhmPi's measurement board on the Raspberry Pi | 
   |        |                                                            |                                                                       
   +--------+------------------------------------------------------------+

.. table::
   :align: center
   
   +--------+------------------------------------------------------------+
   |        |   
   |5       +------------------------------------------------------------+
   |        | Mounting the OhmPi's measurement board on the Raspberry Pi | 
   |        |                                                            |
   +--------+------------------------------------------------------------+   

.. table::
   :align: center
   
   +--------+------------------------------------------------------------+
   |        |   
   |6       +------------------------------------------------------------+
   |        | Plug the power supply into a socket and connect it to your | 
   |        | Raspberry Pi's power port.                                 |
   +--------+------------------------------------------------------------+  

**PART C** Check the measurement board
====================================================== 

 Run the terminal, and write

 .. code-block:: python

     i2cdetect -y 1

.. table::
   :align: center
   
   +--------+------------------------------------------------------------+
   |        |   
   |1       +------------------------------------------------------------+
   |        |If everything is working, three I2C addresses should appear | 
   |        |on the screen.                                              |                                                                       
   +--------+------------------------------------------------------------+

Setting up an equivalent electronic circuit, for this you will need: 
 * 4 1kOhm resistor (R2)
 * 1 220 Ohm resistor (R1)
 * 1 small padboard
 * Spool of solder
 
 .. table::
   :align: left
 
   +--------+------------------------------------------------------------+
   |        |   
   |2       +------------------------------------------------------------+
   |        | Schematic of equivalent electronic circuit test            |                                                                       
   +--------+------------------------------------------------------------+
   
.. table::
   :align: center
 
   +--------+-----------------------------------------------------------------+
   |        |   
   |3       +-----------------------------------------------------------------+
   |        | Prepare the equivalent electronic circuit test                  |                                                                       
   +--------+-----------------------------------------------------------------+ 

.. table::
   :align: center
 
   +--------+-----------------------------------------------------------------+
   |        |   
   |4       +-----------------------------------------------------------------+
   |        |  Prepare the battery connections and the terminals.             |                                                                       
   +--------+-----------------------------------------------------------------+ 

.. table::
   :align: center
 
   +--------+--------------------------------------------------------------------------------+
   |        |   
   |5       +--------------------------------------------------------------------------------+
   |        | Soldering cables and terminals                                                 |                                                                       
   +--------+--------------------------------------------------------------------------------+ 

.. table::
   :align: center
 
   +--------+--------------------------------------------------------------------------------+
   |        |   
   |6       +--------------------------------------------------------------------------------+
   |        |Install the red cables on the +12V terminal and black cable                     |                                                                       
   |        |on the ground terminal. Connect to two different 12V                            |
   |        |batteries                                                                       |
   +--------+--------------------------------------------------------------------------------+ 

.. table::
   :align: center
 
   +--------+--------------------------------------------------------------------------------+
   |        |   
   |7       +--------------------------------------------------------------------------------+
   |        | Connect the equivalent electronic circuit test                                 |                                                                       
   |        |                                                                                |
   +--------+--------------------------------------------------------------------------------+

.. table::
   :align: center
 
   +--------+-------------------------------------------------------------------------------+
   |        |   
   |7       +-------------------------------------------------------------------------------+
   |        | Run the Thonny Interpreter                                                    |                    
   |        |                                                                               |
   +--------+-------------------------------------------------------------------------------+   

.. table::
   :align: center
 
   +--------+------------------------------------------------------------------------------+
   |        |   
   |7       +------------------------------------------------------------------------------+
   |        | Run sample_measurement_example.py example, if everything                     |                    
   |        | works you should  get the following result (220 Ohm)                         |
   +--------+------------------------------------------------------------------------------+

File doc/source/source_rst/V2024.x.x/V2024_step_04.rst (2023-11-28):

.. warning::
    **OhmPi is a participative project open to all, it requires skills in electronics and to respect the safety rules. OhmPi must be assembled in a professional context and by people competent in electronics. The OhmPi team cannot be held responsible for any material or human damage which would be associated with the use or the assembly of OHMPI. The OhmPi team cannot be held responsible if the equipment does not work after assembly.**

**STEP n°4:** assemble the OhmPi
****************************************************
   
.. table::
   :align: center
   
   +--------+------------------------------------------------------------+
   |        |   
   |      1 +------------------------------------------------------------+
   |        |Cut 4 ribbon cables composed of 16 wires each to the proper | 
   |        |length (about 1.5m). Each wire corresponds to an electrode. |                                                                      
   +--------+------------------------------------------------------------+

.. table::
   :align: center

   +--------+------------------------------------------------------------+
   |        |   
   |      2 +------------------------------------------------------------+
   |        |Crimp the ribbon cable on the corresponding idc connector   | 
   |        |with a suitable clamp. Pay attention to the direction of    |
   |        |the cables. Unbalanced IDC connector. The ribbon cable must |
   |        |be perpendicular to the connector.                          |
   +--------+------------------------------------------------------------+
   
.. table::
   :align: center

   +--------+------------------------------------------------------------+
   |        |   
   |      3 +------------------------------------------------------------+
   |        |Example of IDC connector mounting. The wires should run as  | 
   |        |perpendicular as possible to the IDC connector.             |                                                                      
   +--------+------------------------------------------------------------+   

.. table::
   :align: center

   +--------+------------------------------------------------------------+
   |        |   
   |      4 +------------------------------------------------------------+
   |        |Same for a 6 wires ribbon cable of 1 m length.              | 
   |        |                                                            |                                                                      
   +--------+------------------------------------------------------------+  

.. table::
   :align: center

   +--------+------------------------------------------------------------+
   |        |   
   |      5 +------------------------------------------------------------+
   |        |Cut the ribbon cable flush with the IDC connector.          | 
   |        |                                                            |                                                                      
   +--------+------------------------------------------------------------+  

.. table::
   :align: center

   +--------+------------------------------------------------------------+
   |        |   
   |      6 +------------------------------------------------------------+
   |        |Position 9 spacers above the MUX board, and 9 spacers below |
   |        |                                                            |                                                                      
   +        +------------------------------------------------------------+
   |        |   
   |        +------------------------------------------------------------+
   |        |Profile view for mounting the spacers above and below.      | 
   |        |                                                            |                                                                      
   +--------+------------------------------------------------------------+ 

.. table::
   :align: center

   +--------+------------------------------------------------------------+
   |        |   
   |      7 +------------------------------------------------------------+
   |        |Cut a 50 cm long wire of any color (here yellow). Strip and | 
   |        |tin each end of the wire. Install the wire "A" on the screw |
   |        |terminal of MUX board « A ».                                |                                                                                       
   +--------+------------------------------------------------------------+

.. table::
   :align: center

   +--------+------------------------------------------------------------+
   |        |   
   |      8 +------------------------------------------------------------+
   |        |Cut a red wire and a black wire of 50 cm length. Strip, tin | 
   |        |and position the wires on the left screw terminal as shown  |
   |        |in the picture: i)Red wire 12 V, ii) Black wire GND         |                                                                                       
   +--------+------------------------------------------------------------+

.. table::
   :align: center

   +--------+------------------------------------------------------------+
   |        |   
   |      9 +------------------------------------------------------------+
   |        |Mount the 4 ribbon cables (16-wires each) with IDC          | 
   |        |connectors. A small noise is often heard when the IDC       |
   |        |connector is clipped in place.                              |                                                                                       
   +--------+------------------------------------------------------------+

.. table::
   :align: center

   +--------+------------------------------------------------------------+
   |        |   
   |      10+------------------------------------------------------------+
   |        |Mount the ribbon cables with 6-wires with the corresponding | 
   |        |IDC connectors                                              |
   |        |                                                            |                                                                                       
   +--------+------------------------------------------------------------+ 

.. table::
   :align: center

   +--------+------------------------------------------------------------+
   |        |   
   |      11+------------------------------------------------------------+
   |        |Cut a red wire and a black wire of 10 cm length. Strip and  | 
   |        |tin the wires at the ends. Mount the red wire on the 12V    |
   |        |input and the black wire on the GND input on the right      |
   |        |screw terminal.                                             |
   +--------+------------------------------------------------------------+ 

.. table::
   :align: center

   +--------+------------------------------------------------------------+
   |        |   
   |      12+------------------------------------------------------------+
   |        |Mount and fix the second MUX board "B" on the first with    | 
   |        |the help of 9 spacers.                                      |
   |        |                                                            |
   |        |                                                            |                            
   +--------+------------------------------------------------------------+   

.. table::
   :align: center

   +--------+------------------------------------------------------------+
   |        |   
   |      13+------------------------------------------------------------+
   |        |Cut, strip and tin a red wire and a black wire of 10 cm     | 
   |        |length. Mount the wires on the left screw terminal.         |
   |        |Red wire 12V input, black wire GND input.                   |
   |        |Connect the red and black wires from board A to the right   |                            
   |        |screw terminal of board B. Red wire 12V input. Black wire   |   
   |        |GND input.                                                  |
   +--------+------------------------------------------------------------+  

.. table::
   :align: center

   +--------+------------------------------------------------------------+
   |        |   
   |      14+------------------------------------------------------------+
   |        |Crimp a 16 wires IDC connector on the ribbon cable at about | 
   |        |15 cm from the previous connector. Please, pay attention to |
   |        |the direction of the cable before the crimp procedure.      |
   |        |Mount the ribbon cable on the IDC connector on the board.   |                            
   +--------+------------------------------------------------------------+  

.. table::
   :align: center

   +--------+------------------------------------------------------------+
   |        |   
   |      15+------------------------------------------------------------+
   |        |Repeat the operation for the other 3 ribbon cables.         |                  
   +--------+------------------------------------------------------------+ 

.. table::
   :align: center

   +--------+------------------------------------------------------------+
   |        |   
   |      16+------------------------------------------------------------+
   |        |Repeat the operation for the 6 wires ribbon cable.          |                  
   +--------+------------------------------------------------------------+ 

.. table::
   :align: center

   +--------+------------------------------------------------------------+
   |        |   
   |      17+------------------------------------------------------------+
   |        |Cut a 50 cm long wire "here purple" (Color not relevant but | 
   |        |to be defined). Strip and tin the wire at its ends.         |
   |        |Position the wire on the input B of the screw terminal of   |
   |        |the multiplexing board B.                                   |
   +--------+------------------------------------------------------------+ 

.. table::
   :align: center

   +--------+------------------------------------------------------------+
   |        |   
   |      18+------------------------------------------------------------+
   |        |Repeat all these operations for the third MUX board         | 
   |        |called "M".                                                 |           
   +--------+------------------------------------------------------------+    

.. table::
   :align: center

   +--------+------------------------------------------------------------+
   |        |   
   |      19+------------------------------------------------------------+
   |        |Repeat the operations for the fourth MUX Boards. Attention, | 
   |        |it is necessary to position 5 different spacers (here nylon |
   |        |screw hex spacers) in between the “M” board and the “N” MUX |
   |        |Board (as shown on the photograph). Refer to the following  |                            
   |        |photographs for more details on the assembly of the spacers |
   +--------+------------------------------------------------------------+

.. table::
   :align: center

   +--------+------------------------------------------------------------+
   |        |   
   |      20+------------------------------------------------------------+
   |        |When mounting the 4th MUX board ("N"), screws can be placed |
   |        |on the nylon spacers to fix the boards together. Note that  |
   |        |the other spacers could be used for this purpose.           |
   |        |Connect ribbon cables (16 wires) from board 3 to board 4 as |
   |        |previously described. Connect the red wire (12V) of MUX     |                                                 
   |        |board "M" to the 12V terminal of the right screw terminal   |   
   |        |of MUX Board "N". Connect the black wire (GND) of MUX board |
   |        |“M” to the GND screw terminal on MUX board “N”.             |  
   +--------+------------------------------------------------------------+   

.. table::
   :align: center

   +--------+------------------------------------------------------------+
   |        |   
   |      21+------------------------------------------------------------+
   |        |Cut a red wire and a black wire of one meter length. Place  | 
   |        |the red wire on terminal “12V” and the black wire on        |
   |        |terminal “GND” of the left screw terminal. Tie the wires    |
   |        |together.                                                   |                            
   +--------+------------------------------------------------------------+   

.. table::
   :align: center

   +--------+------------------------------------------------------------+
   |        |   
   |      22+------------------------------------------------------------+
   |        |Tie the A, B, M and N wires together                        |                            
   +--------+------------------------------------------------------------+   

.. table::
   :align: center

   +--------+------------------------------------------------------------+
   |        |   
   |      23+------------------------------------------------------------+
   |        |Cut a PVC plate with the following minimum dimensions :     |  
   |        |200 mm * 150 mm * 5 mm                                      |                       
   +--------+------------------------------------------------------------+ 

.. table::
   :align: center

   +--------+------------------------------------------------------------+
   |        |   
   |      24+------------------------------------------------------------+
   |        |Drill the plate to mount it on the remaining metal spacers. |  
   |        |Do not tighten the assembly.                                |                       
   +--------+------------------------------------------------------------+    
   
.. table::
   :align: center

   +--------+------------------------------------------------------------+
   |        |   
   |      25+------------------------------------------------------------+
   |        |Position the Raspberry Pi (RPI) board on the plate so that  |  
   |        |you can access the USB ports. Mark the holes of the RPI     |
   |        |board on the plate for mounting.                            |
   +--------+------------------------------------------------------------+

.. table::
   :align: center

   +--------+------------------------------------------------------------+
   |        |   
   |      26+------------------------------------------------------------+
   |        |Add spacers on the PVC plate.                               |     
   +--------+------------------------------------------------------------+ 

.. table::
   :align: center

   +--------+------------------------------------------------------------+
   |        |   
   |      27+------------------------------------------------------------+
   |        |Attach the PVC plate to the metal spacers with washers      |     
   |        |and nuts.                                                   |                                
   +--------+------------------------------------------------------------+  

.. table::
   :align: center

   +--------+------------------------------------------------------------+
   |        |   
   |      28+------------------------------------------------------------+
   |        |Position and fix the RPI card on the spacers                |     
   +--------+------------------------------------------------------------+     

.. table::
   :align: center

   +--------+------------------------------------------------------------+
   |        |   
   |      29+------------------------------------------------------------+
   |        |Add spacers on the RPI board. The red (12V) and black (GND) |     
   |        |wires coming out of the "M" MUX board must pass under       |    
   |        |the RPI board.                                              |        
   +--------+------------------------------------------------------------+ 

.. table::
   :align: center

   +--------+------------------------------------------------------------+
   |        |   
   |      30+------------------------------------------------------------+
   |        |Place the measurement board on the RPI GPIO outputs and on  |
   |        |the pre-positioned spacers. Note that LEDs are present on   |
   |        |this measurement board with an associated resistance simply |
   |        |for testing purposes (do not consider this temporary        |
   |        |modification of the board). Same for the orange wire        |
   |        |present on the board.                                       |
   +--------+------------------------------------------------------------+  

.. table::
   :align: center

   +--------+------------------------------------------------------------+
   |        |   
   |      31+------------------------------------------------------------+
   |        |Connect the wires " A " (here yellow), " B " (here purple), |
   |        |" M " (here brown) and " N " (here blue) on the             |
   |        |corresponding terminal blocks on the measurement board.     |
   |        |Connect the 6 wires ribbon cable on the measurement board   |
   |        |by passing under the PVC plate.Connect the red and black    |                                                 
   |        |wires to the 12 V and GND terminal block.                   |   
   +--------+------------------------------------------------------------+   

.. table::
   :align: center

   +--------+------------------------------------------------------------+
   |        |   
   |      32+------------------------------------------------------------+
   |        |Top view of the assembly. Add clips to secure the wires     |     
   |        |together.                                                   |
   +--------+------------------------------------------------------------+ 

.. table::
   :align: center

   +--------+------------------------------------------------------------+
   |        |   
   |      33+------------------------------------------------------------+
   |        |Second view.                                                |     
   +--------+------------------------------------------------------------+    

.. table::
   :align: center

   +--------+------------------------------------------------------------+
   |        |   
   |      34+------------------------------------------------------------+
   |        |Zoom in on the connection of the M and N wires.             |     
   +--------+------------------------------------------------------------+ 

.. table::
   :align: center

   +--------+------------------------------------------------------------+
   |        |   
   |      35+------------------------------------------------------------+
   |        |Zoom in on the connection of the A and B wires.             |     
   +--------+------------------------------------------------------------+ 

.. table::
   :align: center

   +--------+------------------------------------------------------------+
   |        |   
   |      36+------------------------------------------------------------+
   |        |Zoom in on the connection of the « 12V » and « GND » wires. |     
   +--------+------------------------------------------------------------+ 

.. table::
   :align: center

   +--------+------------------------------------------------------------+
   |        |   
   |      37+------------------------------------------------------------+
   |        |Fixing the measurement board on the spacers present on the  |
   |        |RPI board.                                                  |
   +--------+------------------------------------------------------------+
   
.. table::
   :align: center

   +--------+------------------------------------------------------------+
   |        |   
   |      38+------------------------------------------------------------+
   |        |Place the SD card containing the OS and the pre-installed   |
   |        |programs. Connect a mouse and a keyboard to the USB inputs  |
   |        |of the RPI board. Connect a monitor to the HDMI output of   |
   |        |the RPI board.                                              |                                                  
   +--------+------------------------------------------------------------+   

.. table::
   :align: center

   +--------+------------------------------------------------------------+
   |        |   
   |      39+------------------------------------------------------------+
   |        |Connect the red and black cables of board A to a 12V        |
   |        |battery or other laboratory power supply delivering a 12VDC |
   |        |voltage.                                                    |
   |        |Enjoy                                                       |
   +--------+------------------------------------------------------------+

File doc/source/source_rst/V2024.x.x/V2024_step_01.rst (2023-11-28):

**STEP n°1** : Raspberry Pi  configuration 
*******************************************

.. warning::
    **OhmPi is a participative project open to all, it requires skills in electronics and to respect the safety rules. OhmPi must be assembled in a professional context and by people competent in electronics. The OhmPi team cannot be held responsible for any material or human damage which would be associated with the use or the assembly of OHMPI. The OhmPi team cannot be held responsible if the equipment does not work after assembly.**

**PART A:** OS installation  
=============================

+----------------------------------------------------+---------------+
| **Required components**                            | **Quantity**  | 
+----------------------------------------------------+---------------+
|Raspberry Pi 4 Model B                              |              1|
+----------------------------------------------------+---------------+
|Micro SD 32 Go                                      |              1|
+----------------------------------------------------+---------------+
|HDMI Cable                                          |              1|
+----------------------------------------------------+---------------+
|Computer mouse                                      |              1|
+----------------------------------------------------+---------------+
|Computer Keyboard                                   |              1|
+----------------------------------------------------+---------------+

The first step is to start up the Raspberry Pi board, including installation of an OS (operating system). 
For this step, the installation instructions are well described on the Raspberry website 

1. Watch the video `how to set up your raspberry Pi <https://www.youtube.com/watch?v=wjWZhV1v3Pk>`_.

2. The authors recommend installing the latest stable and complete version of Raspberry Pi OS (Previously called Raspbian) by using Raspberry Pi Imager.

3. or you can visit this `website <https://projects.raspberrypi.org/en/projects/raspberry-pi-setting-up>`.  

.. note:: 
     All the development tests were performed on Raspberry Pi 3 Model B, we used the following version of Raspbian:

     alternate text

.. warning::
     Once the OS has been installed,  **1-wire, spi and GPIO remote option** must be deactivated and **I2C option** must be activated via the Raspbian GUI settings menu. Failure to carry out this task may cause damage to the relay shield cards during measurements.

**PART B:** Virtual Environment and packages
============================================

A virtual environment is a way to have multiple, parallel instances of the Python interpreter, each with different package sets and different configurations. 
Each virtual environment contains a discrete copy of the Python interpreter, including copies of its support utilities. It also protects your system in case of problems with the packages.

All dependencies are specified in requirements.txt

.. note:: 
     All instructions below should be typed in the terminal

It is first necessary to ensure that the libatlas-base-dev library is installed:

.. code-block:: python

     sudo apt-get install libatlas-base-dev

We strongly recommend users to create a virtual environment to run the code and installed all required dependencies. It can be done either in a directory gathering all virtual environments used on the computer or within the ohmpy directory.

Create the virtual environment:

.. code-block:: python

     python3 -m venv ohmpy

Activate it using the following command:

.. code-block:: python

     source ohmpy/bin/activate

Install packages within the virtual environment. Installing the following package should be sufficient to meet dependencies:

.. code-block:: python
     
     export CFLAGS=-fcommon
     sudo pip install RPi.GPIO adafruit-blinka numpy pandas adafruit-circuitpython-ads1x15 adafruit-circuitpython-tca9548a adafruit-circuitpython-mcp230xx gpiozero

Check that requirements are met using 

.. code-block:: python

     pip list

You should run you code within the virtual environment
to leave the virtual environment simply type:

.. code-block:: python

     deactivate

**PART C:** Activate virtual environment on Thonny (Python IDE)  (on Raspberry Pi)
====================================================================================

If you decided to use a virtual environment, it is necessary to setup Thonny Python IDE the first time you use it.

1- Run the Thonny Python IDE software, Click on raspberry access **menu > programming> Thonny pythonIDE**

2- Thonny opens, Python runs on the root (Python 3.7.3 (/usr/bin/python3))

alternate text

3-Click on **Run>select interpreter**, a new window opens click on interpret

alternate text

4-On the new open windows select **alternative Python3 or virtual environment**

alternate text

5- New buttons appeared, selected **"locate another python executable "**

6- A new window opens, find the folder where there is the python 3 file in the virtual environment folder previously created **/home/pi/ohmpi/bin/python3**.

7- In the **known interpreter** tab the path of the virtual environment should appear

alternate text

8- Close the window by clicking on **ok**.

9- Close Thonny to save modifications

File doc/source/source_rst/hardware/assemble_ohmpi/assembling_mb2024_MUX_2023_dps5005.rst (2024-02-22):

.. warning::
    **OhmPi is a participative project open to all, it requires skills in electronics and to respect the safety rules. OhmPi must be assembled in a professional context and by people competent in electronics. The OhmPi team cannot be held responsible for any material or human damage which would be associated with the use or the assembly of OHMPI. The OhmPi team cannot be held responsible if the equipment does not work after assembly.**

.. _ohmpi_v2024:

Assembling the 64-electrode OhmPi
*********************************
**1 mb2024 + 4 mux2023 + 1 DPS 500)**

TODO :list on tools and components

.. table::
   :align: center
   :widths: 10 30
   
   +--------+------------------------------------------------------------+
   |        |   
   |      1 +------------------------------------------------------------+
   |        |Cut 4 ribbon cables composed of 16 wires each to the proper | 
   |        |length (about 1.5m).                                        |
   |        |                                                            |
   |        |Each wire corresponds to an electrode.                      |                                                                      
   +--------+------------------------------------------------------------+
   |        |   
   |      2 +------------------------------------------------------------+
   |        |Crimp the ribbon cable on the corresponding idc connector   | 
   |        |with a suitable clamp.                                      |
   |        |                                                            |
   |        |Pay attention to the direction ofthe cables. Unbalanced IDC |
   |        |connector.                                                  |
   |        |                                                            |
   |        |The ribbon cable must                                       |
   |        |be perpendicular to the connector.                          |
   +--------+------------------------------------------------------------+
   |        |   
   |      3 +------------------------------------------------------------+
   |        |Example of IDC connector mounting. The wires should run as  | 
   |        |perpendicular as                                            |
   |        |                                                            |
   |        |possible to the IDC connector.                              |                                                                      
   +--------+------------------------------------------------------------+
   |        |   
   |      4 +------------------------------------------------------------+
   |        |Same for a 6 wires ribbon cable of 1 m length.              | 
   |        |                                                            |                                                                      
   +--------+------------------------------------------------------------+  
   |        |   
   |      5 +------------------------------------------------------------+
   |        |Cut the ribbon cable flush with the IDC connector.          | 
   |        |                                                            |                                                                      
   +--------+------------------------------------------------------------+  
   |        |   
   |      6 +------------------------------------------------------------+
   |        |Position 9 spacers above the MUX board, and 9 spacers below |
   |        |                                                            |                                                                      
   +        +------------------------------------------------------------+
   |        |   
   |        +------------------------------------------------------------+
   |        |Profile view for mounting the spacers above and below.      | 
   |        |                                                            |                                                                      
   +--------+------------------------------------------------------------+
   |        |   
   |      7 +------------------------------------------------------------+
   |        |Cut a 50 cm long wire of any color (here yellow).           |
   |        |                                                            |
   |        |Strip and tin each end of the wire. Install the wire "A"    | 
   |        |on the screw terminal of MUX board « A »                    |
   +--------+------------------------------------------------------------+
   |        |   
   |      8 +------------------------------------------------------------+
   |        |Cut a red wire and a black wire of 50 cm length. Strip, tin | 
   |        |                                                            |
   |        |and place the wires on the left screw terminal as shown     |
   |        |                                                            |
   |        |in the picture: i)Red wire 12 V, ii) Black wire GND         |                                                                                       
   +--------+------------------------------------------------------------+
   |        |   
   |      9 +------------------------------------------------------------+
   |        |Mount the 4 ribbon cables (16-wires each) with IDC          | 
   |        |                                                            |
   |        |connectors. A small noise is often heard when the IDC       |
   |        |                                                            |
   |        |connector is clipped in place.                              |                                                                                       
   +--------+------------------------------------------------------------+
   |        |   
   |      10+------------------------------------------------------------+
   |        |Mount the ribbon cables with 6-wires with the corresponding | 
   |        |                                                            |
   |        |IDC connectors                                              |
   |        |                                                            |                                                                                       
   +--------+------------------------------------------------------------+ 
   |        |   
   |      11+------------------------------------------------------------+
   |        |Cut a red wire and a black wire of 10 cm length. Strip and  | 
   |        |                                                            |
   |        |tin the wires at the ends. Mount the red wire on the 12V    |
   |        |                                                            |
   |        |input and the black wire on the GND input on the right      |
   |        |screw terminal.                                             |
   +--------+------------------------------------------------------------+ 
   |        |   
   |      12+------------------------------------------------------------+
   |        |Mount and fix the second MUX board "B" on the first with    | 
   |        |                                                            |
   |        |the help of 9 spacers.                                      |
   +--------+------------------------------------------------------------+
   |        |   
   |      13+------------------------------------------------------------+
   |        |Cut, strip and tin a red wire and a black wire of 10 cm     | 
   |        |                                                            |
   |        |length. Mount the wires on the left screw terminal.         |
   |        |                                                            |
   |        |Red wire 12V input, black wire GND input.                   |
   |        |                                                            |
   |        |Connect the red and black wires from board A to the right   |                            
   |        |                                                            |
   |        |screw terminal of board B. Red wire 12V input. Black wire   |   
   |        |GND input.                                                  |
   +--------+------------------------------------------------------------+  
   |        |   
   |      14+------------------------------------------------------------+
   |        |Crimp a 16 wires IDC connector on the ribbon cable at about | 
   |        |                                                            |
   |        |15 cm from the previous connector. Please, pay attention to |
   |        |                                                            |
   |        |the direction of the cable before the crimp procedure.      |
   |        |                                                            |
   |        |Mount the ribbon cable on the IDC connector on the board.   |                            
   +--------+------------------------------------------------------------+  
   |        |   
   |      15+------------------------------------------------------------+
   |        |Repeat the operation for the other 3 ribbon cables.         |                  
   +--------+------------------------------------------------------------+ 
   |        |   
   |      16+------------------------------------------------------------+
   |        |Repeat the operation for the 6 wires ribbon cable.          |                  
   +--------+------------------------------------------------------------+ 
   |        |   
   |      17+------------------------------------------------------------+
   |        |Cut a 50 cm long wire "here purple" (Color not relevant but | 
   |        |                                                            |
   |        |to be defined). Strip and tin the wire at its ends.         |
   |        |                                                            |
   |        |Position the wire on the input B of the screw terminal of   |
   |        |the multiplexing board B.                                   |
   +--------+------------------------------------------------------------+ 
   |        |   
   |      18+------------------------------------------------------------+
   |        |Repeat all these operations for the third MUX board         | 
   |        |called "M".                                                 |           
   +--------+------------------------------------------------------------+    
   |        |   
   |      19+------------------------------------------------------------+
   |        |Repeat the operations for the fourth MUX Boards. Attention, | 
   |        |                                                            |
   |        |it is necessary to position 5 different spacers (here nylon |
   |        |                                                            |
   |        |screw hex spacers) in between the “M” board and the “N” MUX |
   |        |                                                            |
   |        |Board (as shown on the photograph). Refer to the following  |                            
   |        |                                                            |
   |        |photographs for more details on the assembly of the spacers |
   +--------+------------------------------------------------------------+
   |        |   
   |      20+------------------------------------------------------------+
   |        |When mounting the 4th MUX board ("N"), screws can be placed |
   |        |                                                            |
   |        |on the nylon spacers to fix the boards together. Note that  |
   |        |                                                            |
   |        |the other spacers could be used for this purpose.           |
   |        |                                                            |
   |        |Connect ribbon cables (16 wires) from board 3 to board 4 as |
   |        |                                                            |
   |        |previously described. Connect the red wire (12V) of MUX     |                                                 
   |        |                                                            |
   |        |board "M" to the 12V terminal of the right screw terminal   |   
   |        |                                                            |
   |        |of MUX Board "N". Connect the black wire (GND) of MUX board |
   |        |                                                            |
   |        |“M” to the GND screw terminal on MUX board “N”.             |  
   +--------+------------------------------------------------------------+ 
   |        |   
   |      21+------------------------------------------------------------+
   |        |Cut a red wire and a black wire of one meter length. Place  | 
   |        |                                                            | 
   |        |the red wire on terminal “12V” and the black wire on        |
   |        |                                                            |
   |        |terminal “GND” of the left screw terminal. Tie the wires    |
   |        |together.                                                   |                            
   +--------+------------------------------------------------------------+   
   |        |   
   |      22+------------------------------------------------------------+
   |        |Tie the A, B, M and N wires together                        |                            
   +--------+------------------------------------------------------------+   
   |        |   
   |      23+------------------------------------------------------------+
   |        |Cut a PVC/wood plate with the following minimum dimensions :|  
   |        |410 mm * 280 mm * 4 mm,                                     |
   |        |                                                            |
   |        |and drill hole (M 3.5 mm)                                   |                       
   +--------+------------------------------------------------------------+ 
   |        |   
   |      24+------------------------------------------------------------+
   |        |Fix the PVC plate                                           |  
   +--------+------------------------------------------------------------+ 
   |        |   
   |      25+------------------------------------------------------------+
   |        |Drill holes for fixing Raspberry Pi and measurement board   |  
   +--------+------------------------------------------------------------+ 
   |        |   
   |      26+------------------------------------------------------------+
   |        |Install spacer for Raspberry Pi on the pvc plate            |  
   +--------+------------------------------------------------------------+
   |        |   
   |      27+------------------------------------------------------------+
   |        |Install spacer for measurement board on the pvc plate       |  
   +--------+------------------------------------------------------------+
   |        |   
   |      28+------------------------------------------------------------+
   |        |Fit 9 flat washers and nuts (M3)                            |  
   +--------+------------------------------------------------------------+
   |        |   
   |      29+------------------------------------------------------------+
   |        |Install Raspberry Pi                                        |  
   +--------+------------------------------------------------------------+
   |        |   
   |      30+------------------------------------------------------------+
   |        |Fit 4 spacers (female/female, M3, 11 mm)                    |  
   +--------+------------------------------------------------------------+
   |        |   
   |      31+------------------------------------------------------------+
   |        |Install the measurement board on the Raspberry Pi,          |  
   |        |                                                            |
   |        |     and fix the 4 screws (M3).                             |
   +--------+------------------------------------------------------------+
   |        |   
   |      32+------------------------------------------------------------+
   |        |Fit 3 flat washers and nuts (M3) for measurement board.     |  
   +--------+------------------------------------------------------------+
   |        |   
   |      33+------------------------------------------------------------+
   |        |Connect 12V and GND cable from Mux to Measurement board     |  
   +--------+------------------------------------------------------------+
   |        |   
   |      34+------------------------------------------------------------+
   |        |The choice is yours: position or fix the DPS 5005.          |  
   |        |                                                            |
   |        |connect USB cable between DPS 5005 and Raspberry Pi         |
   +--------+------------------------------------------------------------+
   |        |   
   |      35+------------------------------------------------------------+
   |        |Prepare two wires ( 30 cm, 1.5 mm², black and red), and     |
   |        |                                                            |
   |        |and install two banana plugs                                |
   +--------+------------------------------------------------------------+
   |        |   
   |      36+------------------------------------------------------------+
   |        |This is optional, but you could install a switch on         |
   |        |                                                            |
   |        |the cable connecting to the 12V RX battery.                 |
   +--------+------------------------------------------------------------+
   |        |   
   |      37+------------------------------------------------------------+
   |        |Prepare two wires ( ~15 cm, 1.5 mm², black and red), and    |
   |        |                                                            |
   |        |and install two banana plugs and connect the measurement    |
   |        |                                                            |
   |        |board and the input of DPH5005 (on the back side)           |
   +--------+------------------------------------------------------------+
   |        |   
   |      38+------------------------------------------------------------+
   |        |Prepare two wires ( ~20 cm, 1.5 mm², black and red), and    |
   |        |                                                            |
   |        |and install two banana plugs and connect the measurement    |
   |        |                                                            |
   |        |board (DPS+ and GND) and the output of DPH5005 (front side) |
   +--------+------------------------------------------------------------+
   |        |   
   |      39+------------------------------------------------------------+
   |        |slide ribbon cable between MUX N and PCV plate, and connect |
   |        |                                                            |
   |        |ribbon cable to IDC connector                               |
   +--------+------------------------------------------------------------+
   |        |   
   |      40+------------------------------------------------------------+
   |        |Do not connect the MUX electrode cables to the measurement  |  
   |        |                                                            |
   |        |board.                                                      |
   +--------+------------------------------------------------------------+
   |        |.. image:: ../../../img/v2024.x.x/ohmpi_64/ref_circuit.png  |
   +--------+------------------------------------------------------------+
   |        |   
   |      40+------------------------------------------------------------+
   |        |Connect a equivalent circuit                                |  
   |        |                                                            |
   |        |R2=1kOhm R1=100 ohm                                         |
   +--------+------------------------------------------------------------+

.. warning::
      At this point in the build, we consider that you have followed the instructions in :ref:`Getting-started` section

Please connect both 12 V Battery for RX and TX.

For direct use of Raspberry Pi Connect Screen, mouse and keybord, for remote control use SSH or VNC.

Now it is possible to carry out the first test on a reference circuit.

Write de following python script your OhmPi folder

.. code-block:: python
   
   import os
   import numpy as np
   import time
   import matplotlib.pyplot as plt
   os.chdir("/home/pi/OhmPi")
   from ohmpi.ohmpi import OhmPi
   k = OhmPi()

.. table::
   :align: center
   :widths: 10 30
   
   +--------+------------------------------------------------------------+
   |        |   
   |      41+------------------------------------------------------------+
   |        |If everything is ok, you get the message upper, if not      | 
   |        |                                                            |                                                                   
   |        |check all cable, and battery or refer to troubleshooting    |
   +--------+------------------------------------------------------------+

.. code-block:: python
   
   k.test_mux()

You should hear each of the 256 MUX board relays activate and deactivate 1 at a time.

.. code-block:: python
   
   k.run_measurement(quad=[1,4,2,3], tx_volt = 5., strategy = 'constant', dutycycle=0.5)

A measurement will start, and you should obtain your first measurement, with a value of R = 100 ohm (R1 on the equivalent circuit).

If not check, your cable connection and batteries

You can now connect the 4 cables of each MUX to the screw terminals of the measurement board identified ABMN.

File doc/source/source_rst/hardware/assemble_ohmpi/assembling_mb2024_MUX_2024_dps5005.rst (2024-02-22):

.. warning::
    **OhmPi is a participative project open to all, it requires skills in electronics and to respect the safety rules. OhmPi must be assembled in a professional context and by people competent in electronics. The OhmPi team cannot be held responsible for any material or human damage which would be associated with the use or the assembly of OHMPI. The OhmPi team cannot be held responsible if the equipment does not work after assembly.**

Assembling an OhmPi Lite (32 electrodes)
****************************************

**1 mb2024 + 4 mux2024 + 1 DPS 5005**

Here, we present how to build a 32-electrode OhmPi system using 1 mb.2024, 4 MUX.2024 and 1 DPS5005.
This tutorial aims to illustrate one way of assembling a system using the MUX 2024 boards.
It provides a working base, with room for improvement. Any idea to improve this design is welcome.
Those who wish to build a 16-electrode OhmPi system can neglect steps 8-10, and adjust cable lengths/numbers accordingly.

.. warning::
  In this set-up, the MUX 2024 boards are configured in 2-role modes (see :ref:`2_roles`), so one should make sure that the MUX board are properly configured before going any further.
  Mounting a system with MUX 2024 boards set-up in 4-role modes imply cabling the boards differently as to what is illustrated in this tutorial.

  It is also best to having tested each MUX board individually before mounting them together.

.. table::
   :align: center
   
   +--------------------------------------------------------------------------------------------------------+
   |   
   +--------------------------------------------------------------------------------------------------------+
   |   
   +--------------------------------------------------------------------------------------------------------+
   |   
   +--------------------------------------------------------------------------------------------------------+
   |   
   +--------------------------------------------------------------------------------------------------------+
   |   
   +--------------------------------------------------------------------------------------------------------+
   |   
   +--------------------------------------------------------------------------------------------------------+
   |   
   +--------------------------------------------------------------------------------------------------------+
   |   
   +--------------------------------------------------------------------------------------------------------+
   |   
   +--------------------------------------------------------------------------------------------------------+
   |   
   +--------------------------------------------------------------------------------------------------------+
   |   
   +--------------------------------------------------------------------------------------------------------+
   |   
   +--------------------------------------------------------------------------------------------------------+

.. warning::
      At this point in the build, we consider that you have followed the instructions in :ref:`Getting-started` section

Please connect both 12 V Battery for RX and TX.

For direct use of Raspberry Pi Connect Screen, mouse and keyboard, for remote control use SSH or VNC.

Now it is possible to carry out the first test on a reference circuit. See tests in :ref:`ohmpi_v2024` for more details.

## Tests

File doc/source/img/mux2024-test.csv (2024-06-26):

Name | Power | Type | Multiplexer BLACK probe | Multiplexer RED probe | Expected 4 roles | Expected 2 roles
SC1 | off | continuity | screw terminal GND | screw terminal PWR | no continuity | no continuity
SC2 | off | continuity | screw terminal role x | screw terminal role y | no continuity | no continuity
SC3 | off | continuity | screw terminal role x | screw terminal role xx | no continuity | continuity
SC4 | off | continuity | screw terminal role x | screw terminal role yy | no continuity | no continuity
SC5 | off | continuity | screw terminal role y | screw terminal role xx | no continuity | no continuity
SC6 | off | continuity | screw terminal role y | screw terminal role yy | no continuity | continuity
SC7 | off | continuity | screw terminal role xx | screw terminal role yy | no continuity | no continuity
SC8 | off | continuity | screw terminal elec 1 | screw terminal elec 2 | no continuity | no continuity
SC9 | off | continuity | screw terminal elec 2 | screw terminal elec 3 | no continuity | no continuity
SC10 | off | continuity | screw terminal elec 3 | screw terminal elec 4 | no continuity | no continuity
SC11 | off | continuity | screw terminal elec 4 | screw terminal elec 5 | no continuity | no continuity
SC12 | off | continuity | screw terminal elec 5 | screw terminal elec 6 | no continuity | no continuity
SC13 | off | continuity | screw terminal elec 6 | screw terminal elec 7 | no continuity | no continuity
SC14 | off | continuity | screw terminal elec 7 | screw terminal elec 8 | no continuity | no continuity
SC15 | off | continuity | screw terminal elec 8 | screw terminal elec 9 | no continuity | continuity
SC16 | off | continuity | screw terminal elec 9 | screw terminal elec 10 | no continuity | no continuity
SC17 | off | continuity | screw terminal elec 10 | screw terminal elec 11 | no continuity | no continuity
SC18 | off | continuity | screw terminal elec 11 | screw terminal elec 12 | no continuity | no continuity
SC19 | off | continuity | screw terminal elec 12 | screw terminal elec 13 | no continuity | no continuity
SC20 | off | continuity | screw terminal elec 13 | screw terminal elec 14 | no continuity | no continuity
SC21 | off | continuity | screw terminal elec 14 | screw terminal elec 15 | no continuity | no continuity
SC22 | off | continuity | screw terminal elec 15 | screw terminal elec 16 | no continuity | no continuity
SC23 | off | continuity | screw terminal elec 1 | screw terminal elec 16 | no continuity | continuity
SC24 | off | continuity | screw terminal elec 2 | screw terminal elec 15 | no continuity | continuity
SC25 | off | continuity | screw terminal elec 3 | screw terminal elec 14 | no continuity | continuity
SC26 | off | continuity | screw terminal elec 4 | screw terminal elec 13 | no continuity | continuity
SC27 | off | continuity | screw terminal elec 5 | screw terminal elec 12 | no continuity | continuity
SC28 | off | continuity | screw terminal elec 6 | screw terminal elec 11 | no continuity | continuity
SC29 | off | continuity | screw terminal elec 7 | screw terminal elec 10 | no continuity | continuity
SC30 | off | continuity | screw terminal elec 8 | screw terminal elec 9 | no continuity | continuity
C1 | off | continuity | screw terminal GND | both MCP23017 VSS | continuity | continuity
C2 | off | continuity | screw terminal GND | I2Cext GND | continuity | continuity
C3 | off | continuity | I2Cext SDA | both MCP23017 SDA | continuity | continuity
C4 | off | continuity | I2Cext SDL | both MCP23017 SDL | continuity | continuity
V1 | on | voltage | screw terminal GND | both MCP23017 SDA | 5V | 5V
V2 | on | voltage | screw terminal GND | both MCP23017 SDL | 5V | 5V
V2 | on | voltage | screw terminal GND | both MCP23017 VDD | 5V | 5V

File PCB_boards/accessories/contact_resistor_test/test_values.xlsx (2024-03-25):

1 | A | 500
2 | B | 500
3 | A | 750
4 | B | 750
5 | A | 1000
6 | B | 1000
7 | A | 1250
8 | B | 1250
9 | A | 1500
10 | B | 1500
11 | A | 3000
12 | B | 3000
13 | A | 6000
14 | B | 6000
15 | A | 9000
16 | B | 9000
1 | 4 | 2 | 3 | 2 | 3 | 1 | 4
5 | 8 | 7 | 6 | 7 | 6 | 5 | 8

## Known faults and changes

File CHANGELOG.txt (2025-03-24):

v2024.1.0
- Add OhmPi.test() (#261)
- Add checklist for field installation (doc/_static/ohmpi-checklist.pdf)
- Add coverage.sh that runs .dev/test_all.py integration test (#263)
- Rename headers (#239)
- Rename strategies: "constant" -> "safe", "full_constant" -> "fixed" (#216)
- Remove tx_volt and vab from run_measurement()
- Add 'battery_voltage_tx' column for adjustable voltage.

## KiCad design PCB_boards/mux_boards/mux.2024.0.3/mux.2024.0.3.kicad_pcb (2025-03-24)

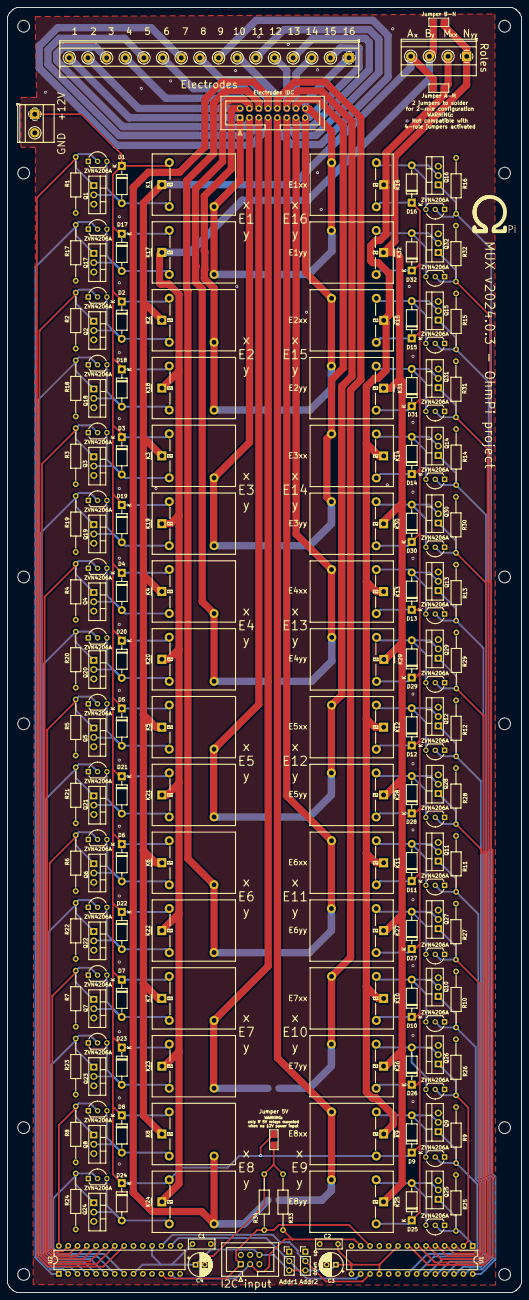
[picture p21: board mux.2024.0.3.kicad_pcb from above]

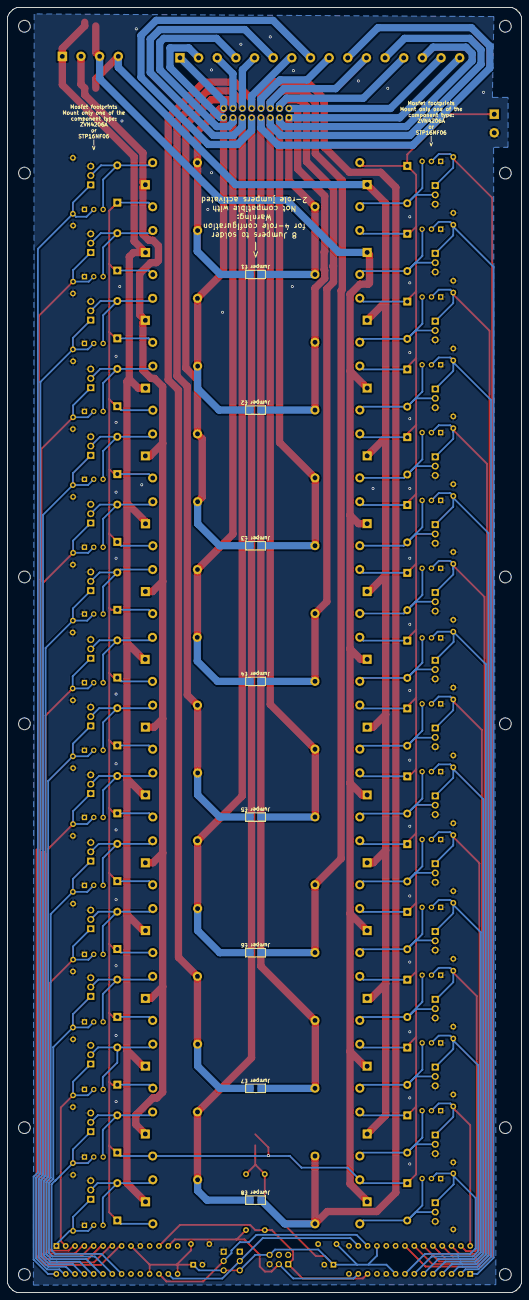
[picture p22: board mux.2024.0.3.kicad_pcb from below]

Board: 2 copper layers, 140.0 x 350.0 mm, 186 parts (8 on the bottom side), 91 nets.

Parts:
A  B  M  N: Screw_Terminal_01x04; TerminalBlock_Phoenix_MKDS-1,5-4-5.08_1x04_P5.08mm_Horizont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
Addr1: Addr 1; PinHeader_1x03_P2.54mm_Vertical
Addr2: Addr 2; PinHeader_1x03_P2.54mm_Vertical
C1, C2: 100nF; C_Disc_D7.0mm_W2.5mm_P5.00mm
C3, C4: 10uF; CP_Radial_D6.3mm_P2.50mm
D1, D2, D3, D4, D5, D6, D7, D8, D9, D10, D11, D12, D13, D14, D15, D16, D17, D18, D19, D20, D21, D22, D23, D24, D25, D26, D27, D28, D29, D30, D31, D32: 1N_E4007; D_DO-41_SOD81_P10.16mm_Horizontal
Electrodes: Screw_Terminal_01x16; TerminalBlock_Phoenix_MKDS-1,5-16-5.08_1x16_P5.08mm_Horizon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
Electrodes IDC: Conn_02x08_Odd_Even; IDC-Header_2x08_P2.54mm_Vertical
GND  +12V: Relays Pwr; TerminalBlock_Phoenix_MKDS-1,5-2-5.08_1x02_P5.08mm_Horizont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
I2C input: I2C; IDC-Header_2x03_P2.54mm_Vertical
Jumper 5V: SolderJumper_2_Open; Soder_jumper
Jumper A-M: SolderJumper_2_Open; Soder_jumper
Jumper B-N: SolderJumper_2_Open; Soder_jumper
Jumper E1, Jumper E2, Jumper E3, Jumper E4, Jumper E5, Jumper E6, Jumper E7, Jumper E8: SolderJumper_2_Open; Soder_jumper
K1, K2, K3, K4, K5, K6, K7, K8, K9, K10, K11, K12, K13, K14, K15, K16, K17, K18, K19, K20, K21, K22, K23, K24, K25, K26, K27, K28, K29, K30, K31, K32: G5LE-1-VD; Relay_SPDT_Omron-G5LE-1-VD
Q1, Q2, Q3, Q4, Q5, Q6, Q7, Q8, Q9, Q10, Q11, Q12, Q13, Q14, Q15, Q16, Q17, Q18, Q19, Q20, Q21, Q22, Q23, Q24, Q25, Q26, Q27, Q28, Q29, Q30, Q31, Q32: STP16NF06L; TO-220-3_Vertical
R1, R2, R3, R4, R5, R6, R7, R8, R9, R10, R11, R12, R13, R14, R15, R16, R17, R18, R19, R20, R21, R22, R23, R24, R25, R26, R27, R28, R29, R30, R31, R32, R33, R34: 100k; R_Axial_DIN0207_L6.3mm_D2.5mm_P15.24mm_Horizontal
U1, U2: MCP23017_SP; DIP-28_W7.62mm
ZVN4206A, ZVN4206A#2, ZVN4206A#3, ZVN4206A#4, ZVN4206A#5, ZVN4206A#6, ZVN4206A#7, ZVN4206A#8, ZVN4206A#9, ZVN4206A#10, ZVN4206A#11, ZVN4206A#12, ZVN4206A#13, ZVN4206A#14, ZVN4206A#15, ZVN4206A#16, ZVN4206A#17, ZVN4206A#18, ZVN4206A#19, ZVN4206A#20, ZVN4206A#21, ZVN4206A#22, ZVN4206A#23, ZVN4206A#24, ZVN4206A#25, ZVN4206A#26, ZVN4206A#27, ZVN4206A#28, ZVN4206A#29, ZVN4206A#30, ZVN4206A#31, ZVN4206A#32: ZVN4206A

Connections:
12V: D1.1 (K), D2.1 (K), D3.1 (K), D4.1 (K), D5.1 (K), D6.1 (K), D7.1 (K), D8.1 (K), D9.1 (K), D10.1 (K), D11.1 (K), D12.1 (K), D13.1 (K), D14.1 (K), D15.1 (K), D16.1 (K), D17.1 (K), D18.1 (K), D19.1 (K), D20.1 (K), D21.1 (K), D22.1 (K), D23.1 (K), D24.1 (K), D25.1 (K), D26.1 (K), D27.1 (K), D28.1 (K), D29.1 (K), D30.1 (K), D31.1 (K), D32.1 (K), GND +12V.1, Jumper 5V.2 (B), K1.5, K2.5, K3.5, K4.5, K5.5, K6.5, K7.5, K8.5, K9.5, K10.5, K11.5, K12.5, K13.5, K14.5, K15.5, K16.5, K17.5, K18.5, K19.5, K20.5, K21.5, K22.5, K23.5, K24.5, K25.5, K26.5, K27.5, K28.5, K29.5, K30.5, K31.5, K32.5
+5V: Addr1.3 (B), Addr2.3 (B), C1.1, C2.1, C3.1, C4.1, I2C input.6, Jumper 5V.1 (A), R33.1, R34.1, U1.9 (VDD), U1.15 (A0), U1.18 (~RESET), U2.9 (VDD), U2.18 (~RESET)
Addr1: Addr1.2 (C), U1.16 (A1), U2.16 (A1)
Addr2: Addr2.2 (C), U1.17 (A2), U2.17 (A2)
E1x: Q1.1 (G), R1.1, U2.21 (GPA0), ZVN4206A#27.2
E1y: Q17.1 (G), R17.1, U2.1 (GPB0), ZVN4206A#7.2
E2x: Q2.1 (G), R2.1, U2.22 (GPA1), ZVN4206A#6.2
E2y: Q18.1 (G), R18.1, U2.2 (GPB1), ZVN4206A#32.2
E3x: Q3.1 (G), R3.1, U2.23 (GPA2), ZVN4206A#31.2
E3y: Q19.1 (G), R19.1, U2.3 (GPB2), ZVN4206A#9.2
E4x: Q4.1 (G), R4.1, U2.24 (GPA3), ZVN4206A#5.2
E4y: Q20.1 (G), R20.1, U2.4 (GPB3), ZVN4206A#12.2
E5x: Q5.1 (G), R5.1, U2.25 (GPA4), ZVN4206A#26.2
E5y: Q21.1 (G), R21.1, U2.5 (GPB4), ZVN4206A#8.2
E6x: Q6.1 (G), R6.1, U2.26 (GPA5), ZVN4206A#22.2
E6y: Q22.1 (G), R22.1, U2.6 (GPB5), ZVN4206A#11.2
E7x: Q7.1 (G), R7.1, U2.27 (GPA6), ZVN4206A#17.2
E7y: Q23.1 (G), R23.1, U2.7 (GPB6), ZVN4206A#30.2
E8x: Q8.1 (G), R8.1, U2.28 (GPA7), ZVN4206A#2.2
E8y: Q24.1 (G), R24.1, U2.8 (GPB7), ZVN4206A#21.2
E9x: Q9.1 (G), R9.1, U1.21 (GPA0), ZVN4206A#24.2
E9y: Q25.1 (G), R25.1, U1.1 (GPB0), ZVN4206A#28.2
E10x: Q10.1 (G), R10.1, U1.22 (GPA1), ZVN4206A#25.2
E10y: Q26.1 (G), R26.1, U1.2 (GPB1), ZVN4206A#20.2
E11x: Q11.1 (G), R11.1, U1.23 (GPA2), ZVN4206A.2
E11y: Q27.1 (G), R27.1, U1.3 (GPB2), ZVN4206A#10.2
E12x: Q12.1 (G), R12.1, U1.24 (GPA3), ZVN4206A#18.2
E12y: Q28.1 (G), R28.1, U1.4 (GPB3), ZVN4206A#29.2
E13x: Q13.1 (G), R13.1, U1.25 (GPA4), ZVN4206A#13.2
E13y: Q29.1 (G), R29.1, U1.5 (GPB4), ZVN4206A#19.2
E14x: Q14.1 (G), R14.1, U1.26 (GPA5), ZVN4206A#16.2
E14y: Q30.1 (G), R30.1, U1.6 (GPB5), ZVN4206A#14.2
E15x: Q15.1 (G), R15.1, U1.27 (GPA6), ZVN4206A#4.2
E15y: Q31.1 (G), R31.1, U1.7 (GPB6), ZVN4206A#3.2
E16x: Q16.1 (G), R16.1, U1.28 (GPA7), ZVN4206A#15.2
E16y: Q32.1 (G), R32.1, U1.8 (GPB7), ZVN4206A#23.2
Electrode 1: Electrodes.16, Electrodes IDC.1, Jumper E1.1 (A), K1.3, K17.3
Electrode 2: Electrodes.15, Electrodes IDC.2, Jumper E2.1 (A), K2.3, K18.3
Electrode 3: Electrodes.14, Electrodes IDC.3, Jumper E3.1 (A), K3.3, K19.3
Electrode 4: Electrodes.13, Electrodes IDC.4, Jumper E4.1 (A), K4.3, K20.3
Electrode 5: Electrodes.12, Electrodes IDC.5, Jumper E5.1 (A), K5.3, K21.3
Electrode 6: Electrodes.11, Electrodes IDC.6, Jumper E6.1 (A), K6.3, K22.3
Electrode 7: Electrodes.10, Electrodes IDC.7, Jumper E7.1 (A), K7.3, K23.3
Electrode 8: Electrodes.9, Electrodes IDC.8, Jumper E8.1 (A), K8.3, K24.3
Electrode 9: Electrodes.8, Electrodes IDC.9, Jumper E8.2 (B), K9.3, K25.3
Electrode 10: Electrodes.7, Electrodes IDC.10, Jumper E7.2 (B), K10.3, K26.3
Electrode 11: Electrodes.6, Electrodes IDC.11, Jumper E6.2 (B), K11.3, K27.3
Electrode 12: Electrodes.5, Electrodes IDC.12, Jumper E5.2 (B), K12.3, K28.3
Electrode 13: Electrodes.4, Electrodes IDC.13, Jumper E4.2 (B), K13.3, K29.3
Electrode 14: Electrodes.3, Electrodes IDC.14, Jumper E3.2 (B), K14.3, K30.3
Electrode 15: Electrodes.2, Electrodes IDC.15, Jumper E2.2 (B), K15.3, K31.3
Electrode 16: Electrodes.1, Electrodes IDC.16, Jumper E1.2 (B), K16.3, K32.3
GND: Addr1.1 (A), Addr2.1 (A), C1.2, C2.2, C3.2, C4.2, GND +12V.2, I2C input.5, Q1.3 (S), Q2.3 (S), Q3.3 (S), Q4.3 (S), Q5.3 (S), Q6.3 (S), Q7.3 (S), Q8.3 (S), Q9.3 (S), Q10.3 (S), Q11.3 (S), Q12.3 (S), Q13.3 (S), Q14.3 (S), Q15.3 (S), Q16.3 (S), Q17.3 (S), Q18.3 (S), Q19.3 (S), Q20.3 (S), Q21.3 (S), Q22.3 (S), Q23.3 (S), Q24.3 (S), Q25.3 (S), Q26.3 (S), Q27.3 (S), Q28.3 (S), Q29.3 (S), Q30.3 (S), Q31.3 (S), Q32.3 (S), R1.2, R2.2, R3.2, R4.2, R5.2, R6.2, R7.2, R8.2, R9.2, R10.2, R11.2, R12.2, R13.2, R14.2, R15.2, R16.2, R17.2, R18.2, R19.2, R20.2, R21.2, R22.2, R23.2, R24.2, R25.2, R26.2, R27.2, R28.2, R29.2, R30.2, R31.2, R32.2, U1.10 (VSS), U2.10 (VSS), U2.15 (A0), ZVN4206A.3, ZVN4206A#2.3, ZVN4206A#3.3, ZVN4206A#4.3, ZVN4206A#5.3, ZVN4206A#6.3, ZVN4206A#7.3, ZVN4206A#8.3, ZVN4206A#9.3, ZVN4206A#10.3, ZVN4206A#11.3, ZVN4206A#12.3, ZVN4206A#13.3, ZVN4206A#14.3, ZVN4206A#15.3, ZVN4206A#16.3, ZVN4206A#17.3, ZVN4206A#18.3, ZVN4206A#19.3, ZVN4206A#20.3, ZVN4206A#21.3, ZVN4206A#22.3, ZVN4206A#23.3, ZVN4206A#24.3, ZVN4206A#25.3, ZVN4206A#26.3, ZVN4206A#27.3, ZVN4206A#28.3, ZVN4206A#29.3, ZVN4206A#30.3, ZVN4206A#31.3, ZVN4206A#32.3
unnamed: D1.2 (A), K1.2, Q1.2 (D), ZVN4206A#27.1
unnamed: D2.2 (A), K2.2, Q2.2 (D), ZVN4206A#6.1
unnamed: D3.2 (A), K3.2, Q3.2 (D), ZVN4206A#31.1
unnamed: D4.2 (A), K4.2, Q4.2 (D), ZVN4206A#5.1
unnamed: D5.2 (A), K5.2, Q5.2 (D), ZVN4206A#26.1
unnamed: D6.2 (A), K6.2, Q6.2 (D), ZVN4206A#22.1
unnamed: D7.2 (A), K7.2, Q7.2 (D), ZVN4206A#17.1
unnamed: D8.2 (A), K8.2, Q8.2 (D), ZVN4206A#2.1
unnamed: D9.2 (A), K9.2, Q9.2 (D), ZVN4206A#24.1
unnamed: D10.2 (A), K10.2, Q10.2 (D), ZVN4206A#25.1
unnamed: D11.2 (A), K11.2, Q11.2 (D), ZVN4206A.1
unnamed: D12.2 (A), K12.2, Q12.2 (D), ZVN4206A#18.1
unnamed: D13.2 (A), K13.2, Q13.2 (D), ZVN4206A#13.1
unnamed: D14.2 (A), K14.2, Q14.2 (D), ZVN4206A#16.1
unnamed: D15.2 (A), K15.2, Q15.2 (D), ZVN4206A#4.1
unnamed: D16.2 (A), K16.2, Q16.2 (D), ZVN4206A#15.1
unnamed: D17.2 (A), K17.2, Q17.2 (D), ZVN4206A#7.1
unnamed: D18.2 (A), K18.2, Q18.2 (D), ZVN4206A#32.1
unnamed: D19.2 (A), K19.2, Q19.2 (D), ZVN4206A#9.1
unnamed: D20.2 (A), K20.2, Q20.2 (D), ZVN4206A#12.1
unnamed: D21.2 (A), K21.2, Q21.2 (D), ZVN4206A#8.1
unnamed: D22.2 (A), K22.2, Q22.2 (D), ZVN4206A#11.1
unnamed: D23.2 (A), K23.2, Q23.2 (D), ZVN4206A#30.1
unnamed: D24.2 (A), K24.2, Q24.2 (D), ZVN4206A#21.1
unnamed: D25.2 (A), K25.2, Q25.2 (D), ZVN4206A#28.1
unnamed: D26.2 (A), K26.2, Q26.2 (D), ZVN4206A#20.1
unnamed: D27.2 (A), K27.2, Q27.2 (D), ZVN4206A#10.1
unnamed: D28.2 (A), K28.2, Q28.2 (D), ZVN4206A#29.1
unnamed: D29.2 (A), K29.2, Q29.2 (D), ZVN4206A#19.1
unnamed: D30.2 (A), K30.2, Q30.2 (D), ZVN4206A#14.1
unnamed: D31.2 (A), K31.2, Q31.2 (D), ZVN4206A#3.1
unnamed: D32.2 (A), K32.2, Q32.2 (D), ZVN4206A#23.1
Role x: A B M N.4, Jumper A-M.1 (A), K1.1, K2.1, K3.1, K4.1, K5.1, K6.1, K7.1, K8.1
Role xx: A B M N.2, Jumper A-M.2 (B), K9.1, K10.1, K11.1, K12.1, K13.1, K14.1, K15.1, K16.1
Role y: A B M N.3, Jumper B-N.1 (A), K17.1, K18.1, K19.1, K20.1, K21.1, K22.1, K23.1, K24.1
Role yy: A B M N.1, Jumper B-N.2 (B), K25.1, K26.1, K27.1, K28.1, K29.1, K30.1, K31.1, K32.1
SCL1: I2C input.1, R34.2, U1.12 (SCK), U2.12 (SCK)
SD1: I2C input.3, R33.2, U1.13 (SDA), U2.13 (SDA)

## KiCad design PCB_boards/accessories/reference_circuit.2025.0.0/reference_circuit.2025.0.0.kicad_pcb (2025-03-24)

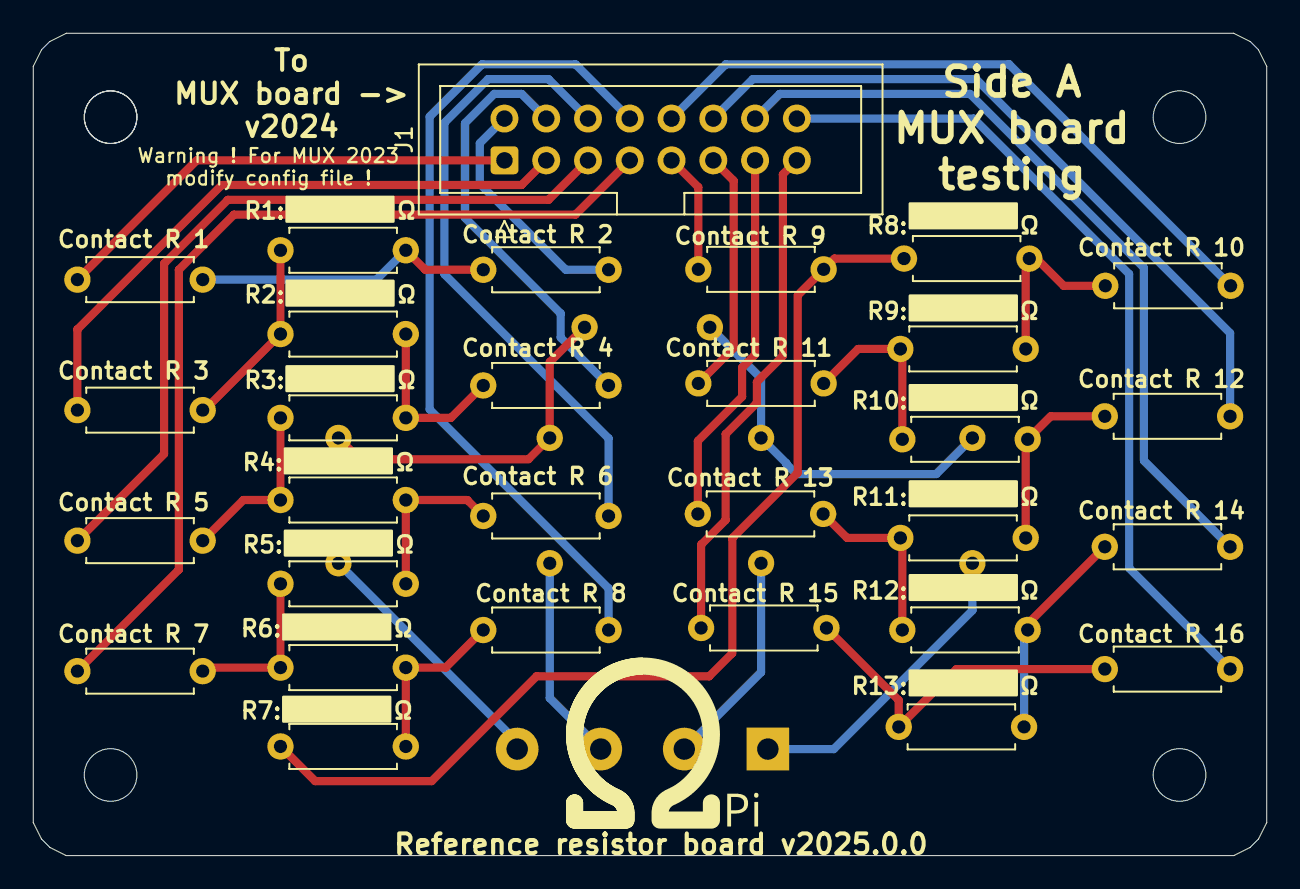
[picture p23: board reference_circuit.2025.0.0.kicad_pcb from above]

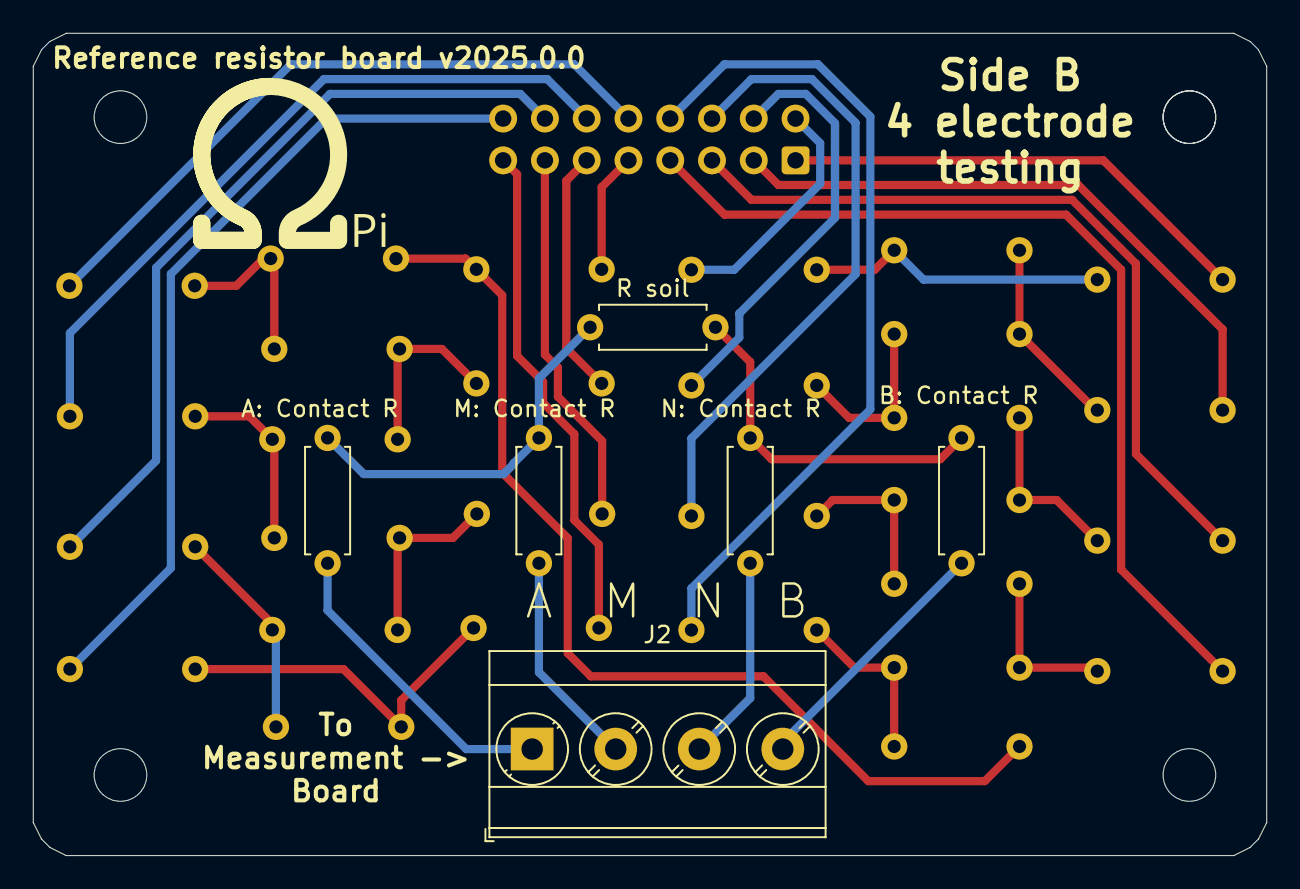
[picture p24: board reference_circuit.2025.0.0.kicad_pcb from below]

Board: 2 copper layers, 75.0 x 50.0 mm, 36 parts (6 on the bottom side), 36 nets.

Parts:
A: Contact R: R; R_Axial_DIN0207_L6.3mm_D2.5mm_P7.62mm_Horizontal
B: Contact R: R; R_Axial_DIN0207_L6.3mm_D2.5mm_P7.62mm_Horizontal
J1: Conn_02x08_Odd_Even; IDC-Header_2x08_P2.54mm_Vertical
J2: Screw_Terminal_01x04; TerminalBlock_Phoenix_MKDS-3-4-5.08_1x04_P5.08mm_Horizontal
M: Contact R: R; R_Axial_DIN0207_L6.3mm_D2.5mm_P7.62mm_Horizontal
N: Contact R: R; R_Axial_DIN0207_L6.3mm_D2.5mm_P7.62mm_Horizontal
R1, R2, R3, R4, R5, R6, R7, R8, R9, R10, R11, R12, R13, R14, R15, R16, R18, R19, R20, R21, R22, R23, R24, R25, R26, R27, R28, R29, R30: R; R_Axial_DIN0207_L6.3mm_D2.5mm_P7.62mm_Horizontal
R soil: R; R_Axial_DIN0207_L6.3mm_D2.5mm_P7.62mm_Horizontal

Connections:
unnamed: J1.1, R1.1
unnamed: J1.2, R2.1
unnamed: J1.3, R3.1
unnamed: J1.4, R4.1
unnamed: J1.5, R5.1
unnamed: J1.6, R6.1
unnamed: J1.7, R7.1
unnamed: J1.8, R8.1
unnamed: J1.9, R9.1
unnamed: J1.10, R10.1
unnamed: J1.11, R11.1
unnamed: J1.12, R12.1
unnamed: J1.13, R13.1
unnamed: J1.14, R14.1
unnamed: J1.15, R15.1
unnamed: J1.16, R16.1
unnamed: A: Contact R.1, J2.1
unnamed: J2.2, M: Contact R.1
unnamed: J2.3, N: Contact R.1
unnamed: B: Contact R.1, J2.4
unnamed: R1.2, R2.2, R18.1
unnamed: R10.2, R25.2, R26.1
unnamed: R11.2, R26.2, R27.1
unnamed: R12.2, R27.2, R28.1
unnamed: R13.2, R28.2, R29.1
unnamed: R14.2, R29.2, R30.1
unnamed: R15.2, R16.2, R30.2
unnamed: R3.2, R18.2, R19.1
unnamed: R4.2, R19.2, R20.1
unnamed: R5.2, R20.2, R21.1
unnamed: R6.2, R21.2, R22.1
unnamed: R7.2, R22.2, R23.1
unnamed: R8.2, R23.2, R24.1
unnamed: R9.2, R24.2, R25.1
unnamed: A: Contact R.2, M: Contact R.2, R soil.1
unnamed: B: Contact R.2, N: Contact R.2, R soil.2

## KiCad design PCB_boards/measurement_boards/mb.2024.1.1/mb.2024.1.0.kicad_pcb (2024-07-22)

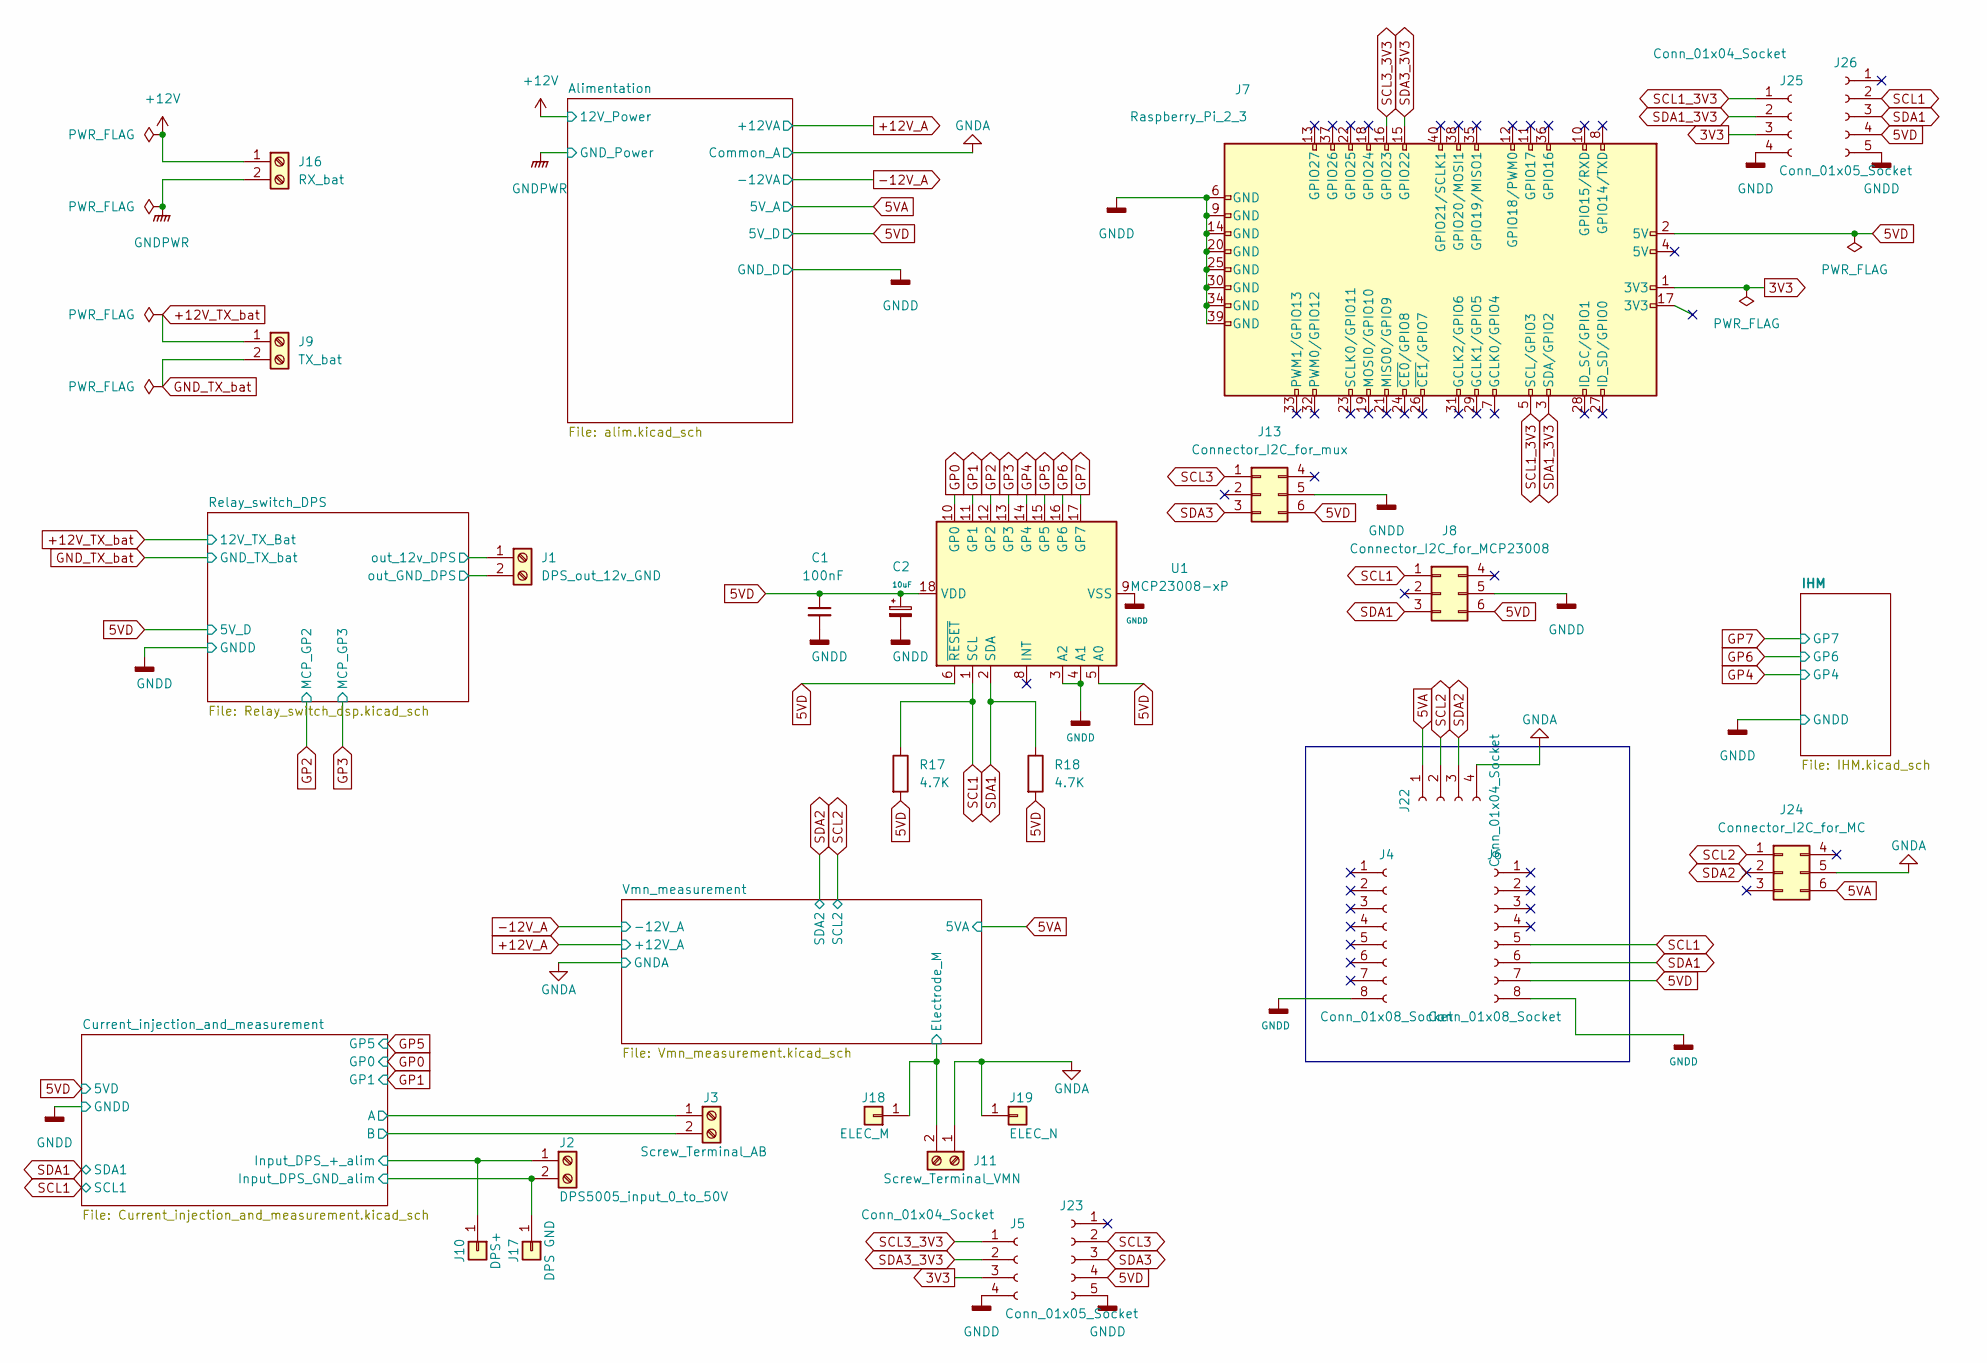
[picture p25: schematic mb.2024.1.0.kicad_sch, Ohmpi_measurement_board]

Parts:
C1: 100nF; C_Disc_D8.0mm_W2.5mm_P5.00mm
C2: 10uF; CP_Radial_D6.3mm_P2.50mm
J1: DPS_out_12v_GND; TerminalBlock_Phoenix_MKDS-1,5-2-5.08_1x02_P5.08mm_Horizont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
J2: DPS5005_input_0_to_50V; TerminalBlock_Phoenix_MKDS-1,5-2-5.08_1x02_P5.08mm_Horizont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
J3: Screw_Terminal_AB; TerminalBlock_Phoenix_MKDS-1,5-2-5.08_1x02_P5.08mm_Horizont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
J4, J6: Conn_01x08_Socket; PinHeader_1x08_P2.54mm_Vertical
J5, J22, J25: Conn_01x04_Socket; PinHeader_1x04_P2.54mm_Vertical
J7: Raspberry_Pi_2_3; PinSocket_2x20_P2.54mm_Vertical
J8: Connector_I2C_for_MCP23008; IDC-Header_2x03_P2.54mm_Vertical
J9: TX_bat; TerminalBlock_Phoenix_MKDS-1,5-2-5.08_1x02_P5.08mm_Horizont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
J10: DPS+; PinHeader_1x01_P2.54mm_Vertical
J11: Screw_Terminal_VMN; TerminalBlock_Phoenix_MKDS-1,5-2-5.08_1x02_P5.08mm_Horizont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
J13: Connector_I2C_for_mux; IDC-Header_2x03_P2.54mm_Vertical
J16: RX_bat; TerminalBlock_Phoenix_MKDS-1,5-2-5.08_1x02_P5.08mm_Horizont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
J17: DPS GND; PinHeader_1x01_P2.54mm_Vertical
J18: ELEC_M; PinHeader_1x01_P2.54mm_Vertical
J19: ELEC_N; PinHeader_1x01_P2.54mm_Vertical
J23, J26: Conn_01x05_Socket; PinHeader_1x05_P2.54mm_Vertical
J24: Connector_I2C_for_MC; IDC-Header_2x03_P2.54mm_Vertical
R17, R18: 4.7K; R_Axial_DIN0207_L6.3mm_D2.5mm_P7.62mm_Horizontal
U1: MCP23008-xP; DIP-18_W7.62mm

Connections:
3V3: J5.3, J7.1 (3V3), J25.3
5VA: J22.1, J24.6; also elsewhere on the board
5VD: C1.1, C2.1, J6.7, J7.2 (5V), J8.6, J13.6, J23.4, J26.4, R17.2, R18.2, U1.5 (A0), U1.6 (~RESET), U1.18 (VDD); also elsewhere on the board
+12V: J16.1; also elsewhere on the board
+12V_TX_bat: J9.1; also elsewhere on the board
/Current_injection_and_measurement/A: J3.1; also elsewhere on the board
/Current_injection_and_measurement/B: J3.2; also elsewhere on the board
/Current_injection_and_measurement/Input_DPS_+_alim: J2.1, J10.1; also elsewhere on the board
/Current_injection_and_measurement/Input_DPS_GND_alim: J2.2, J17.1; also elsewhere on the board
/Relay_switch_DPS/out_12v_DPS: J1.1; also elsewhere on the board
/Relay_switch_DPS/out_GND_DPS: J1.2; also elsewhere on the board
/Vmn_measurement/Electrode_M: J11.2, J18.1; also elsewhere on the board
GNDA: J11.1, J19.1, J22.4, J24.5; also elsewhere on the board
GNDD: C1.2, C2.2, J4.8, J5.4, J6.8, J7.6 (GND), J7.9 (GND), J7.14 (GND), J7.20 (GND), J7.25 (GND), J7.30 (GND), J7.34 (GND), J7.39 (GND), J8.5, J13.5, J23.5, J25.4, J26.5, U1.3 (A2), U1.4 (A1), U1.9 (VSS); also elsewhere on the board
GNDPWR: J16.2; also elsewhere on the board
GND_TX_bat: J9.2; also elsewhere on the board
GP0: U1.10 (GP0); also elsewhere on the board
GP1: U1.11 (GP1); also elsewhere on the board
GP2: U1.12 (GP2); also elsewhere on the board
GP3: U1.13 (GP3); also elsewhere on the board
GP4: U1.14 (GP4); also elsewhere on the board
GP5: U1.15 (GP5); also elsewhere on the board
GP6: U1.16 (GP6); also elsewhere on the board
GP7: U1.17 (GP7); also elsewhere on the board
SCL1: J6.5, J8.1, J26.2, R17.1, U1.1 (SCL); also elsewhere on the board
SCL1_3V3: J7.5 (SCL/GPIO3), J25.1
SCL2: J22.2, J24.1; also elsewhere on the board
SCL3: J13.1, J23.2
SCL3_3V3: J5.1, J7.16 (GPIO23)
SDA1: J6.6, J8.3, J26.3, R18.1, U1.2 (SDA); also elsewhere on the board
SDA1_3V3: J7.3 (SDA/GPIO2), J25.2
SDA2: J22.3, J24.2; also elsewhere on the board
SDA3: J13.3, J23.3
SDA3_3V3: J5.2, J7.15 (GPIO22)

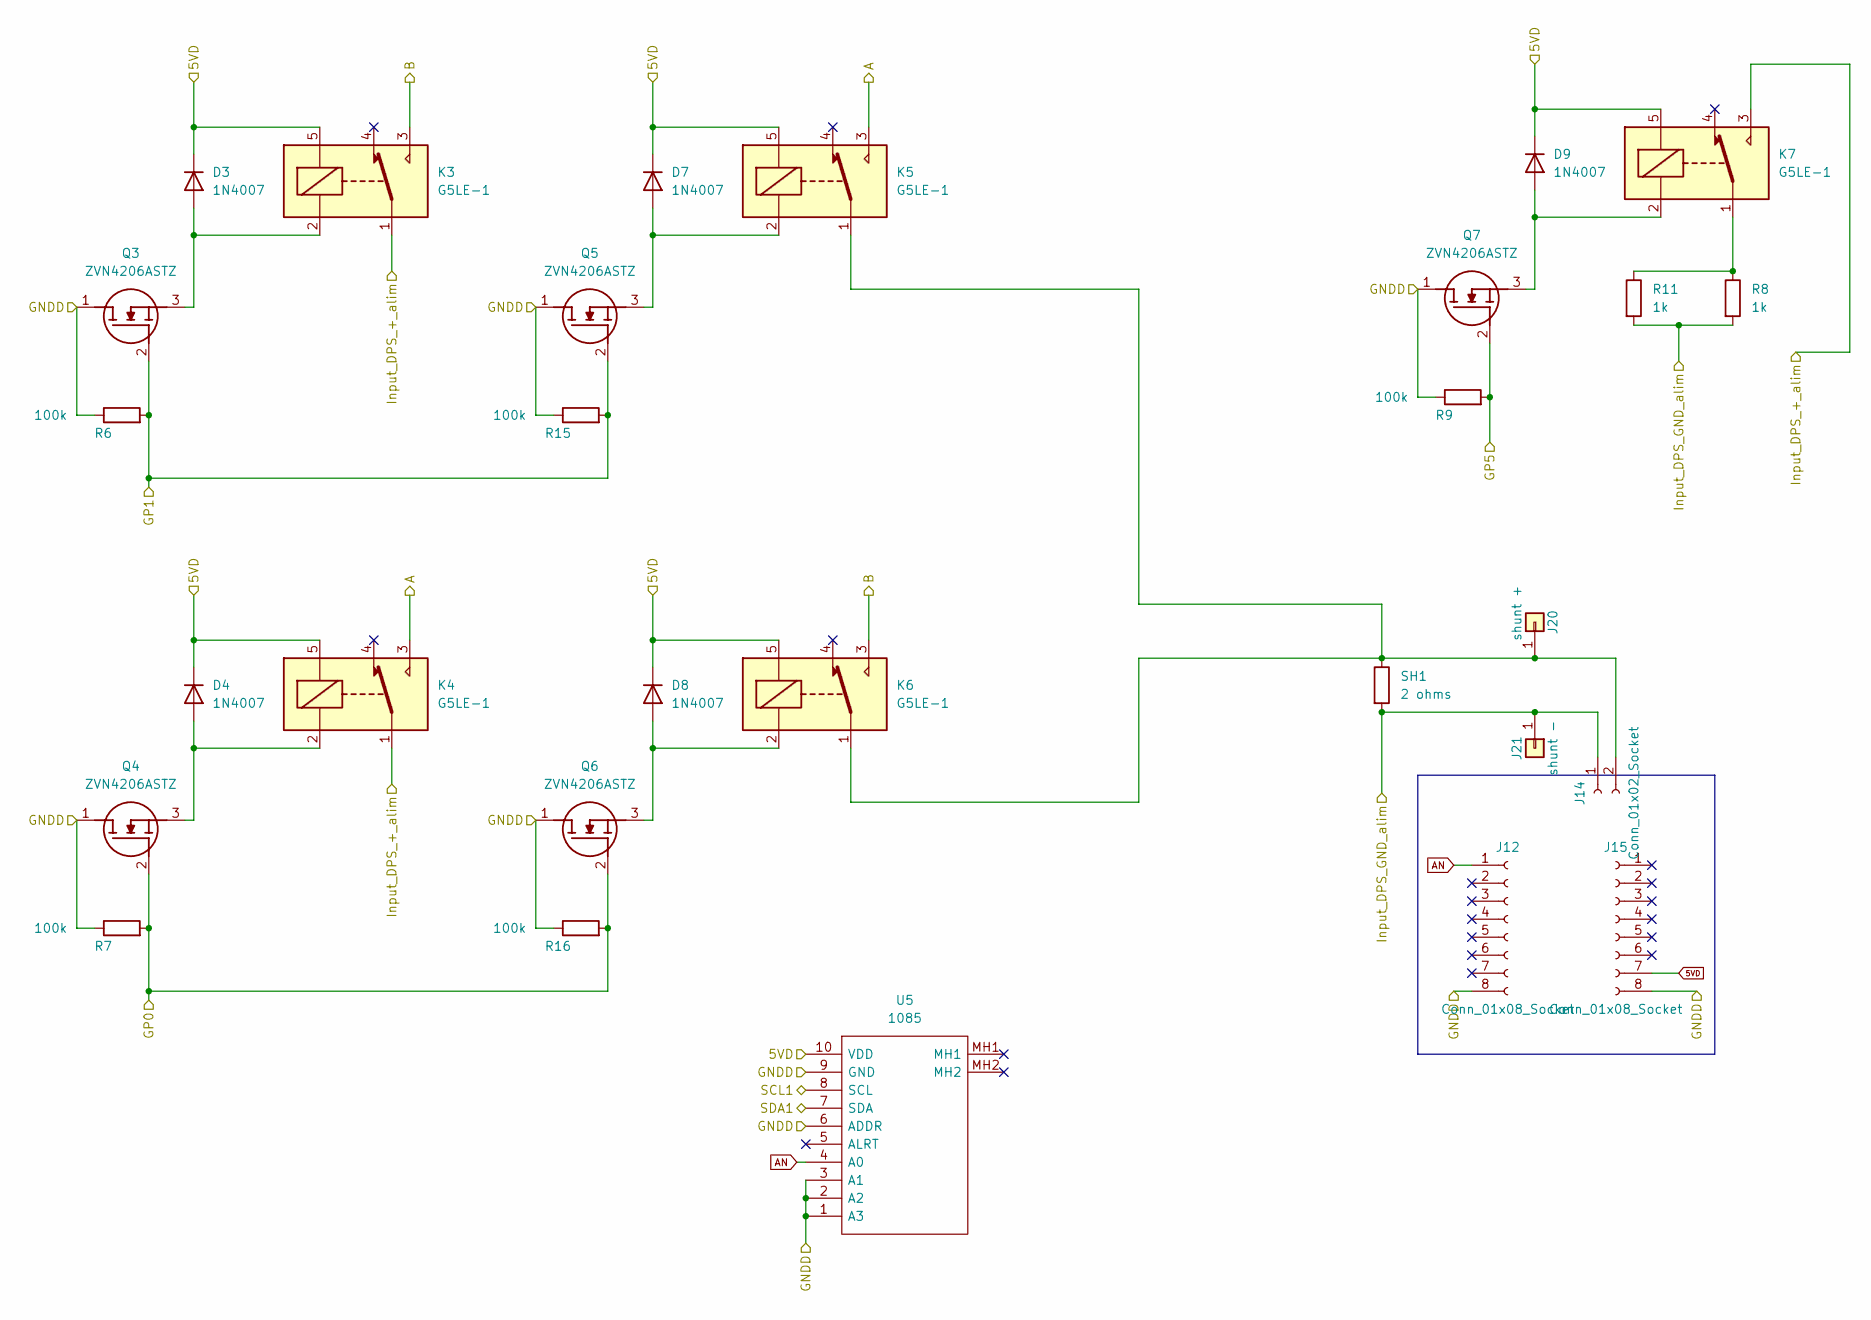
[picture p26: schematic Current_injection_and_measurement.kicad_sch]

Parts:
D3, D4, D7, D8, D9: 1N4007; D_DO-41_SOD81_P10.16mm_Horizontal
J12, J15: Conn_01x08_Socket; PinHeader_1x08_P2.54mm_Vertical
J14: Conn_01x02_Socket; PinHeader_1x02_P2.54mm_Vertical
J20: shunt +; PinHeader_1x01_P2.54mm_Vertical
J21: shunt -; PinHeader_1x01_P2.54mm_Vertical
K3, K4, K5, K6, K7: G5LE-1; Relay_SPDT_Omron-G5LE-1
Q3, Q4, Q5, Q6, Q7: ZVN4206ASTZ; TO-92L_Wide; Manufacturer_Part_Number ZVN4206ASTZ; Mouser Part Number 522-ZVN4206ASTZ
R6, R7, R9, R15, R16: 100k; R_Axial_DIN0207_L6.3mm_D2.5mm_P7.62mm_Horizontal
R8, R11: 1k; R_Axial_DIN0207_L6.3mm_D2.5mm_P7.62mm_Horizontal
SH1: 2 ohms; R_Axial_DIN0414_L11.9mm_D4.5mm_P20.32mm_Horizontal
U5: 1085; Manufacturer_Part_Number 1085; Mouser Part Number 485-1085

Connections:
5VD: D3.1 (K), D4.1 (K), D7.1 (K), D8.1 (K), D9.1 (K), J15.7, K3.5, K4.5, K5.5, K6.5, K7.5, U5.10 (VDD); also elsewhere on the board
/Current_injection_and_measurement/A: K4.3, K5.3; also elsewhere on the board
/Current_injection_and_measurement/B: K3.3, K6.3; also elsewhere on the board
/Current_injection_and_measurement/Input_DPS_+_alim: K3.1, K4.1, K7.3; also elsewhere on the board
/Current_injection_and_measurement/Input_DPS_GND_alim: J14.1, J21.1, R8.2, R11.2, SH1.2; also elsewhere on the board
AN: J12.1, U5.4 (A0)
GNDD: J12.8, J15.8, Q3.1 (D), Q4.1 (D), Q5.1 (D), Q6.1 (D), Q7.1 (D), R6.1, R7.1, R9.1, R15.1, R16.1, U5.1 (A3), U5.2 (A2), U5.3 (A1), U5.6 (ADDR), U5.9 (GND); also elsewhere on the board
GP0: Q4.2 (G), Q6.2 (G), R7.2, R16.2; also elsewhere on the board
GP1: Q3.2 (G), Q5.2 (G), R6.2, R15.2; also elsewhere on the board
GP5: Q7.2 (G), R9.2; also elsewhere on the board
unnamed: D3.2 (A), K3.2, Q3.3 (S)
unnamed: D4.2 (A), K4.2, Q4.3 (S)
unnamed: D7.2 (A), K5.2, Q5.3 (S)
unnamed: D8.2 (A), K6.2, Q6.3 (S)
unnamed: D9.2 (A), K7.2, Q7.3 (S)
unnamed: J14.2, J20.1, K5.1, K6.1, SH1.1
unnamed: K7.1, R8.1, R11.1
SCL1: U5.8 (SCL); also elsewhere on the board
SDA1: U5.7 (SDA); also elsewhere on the board

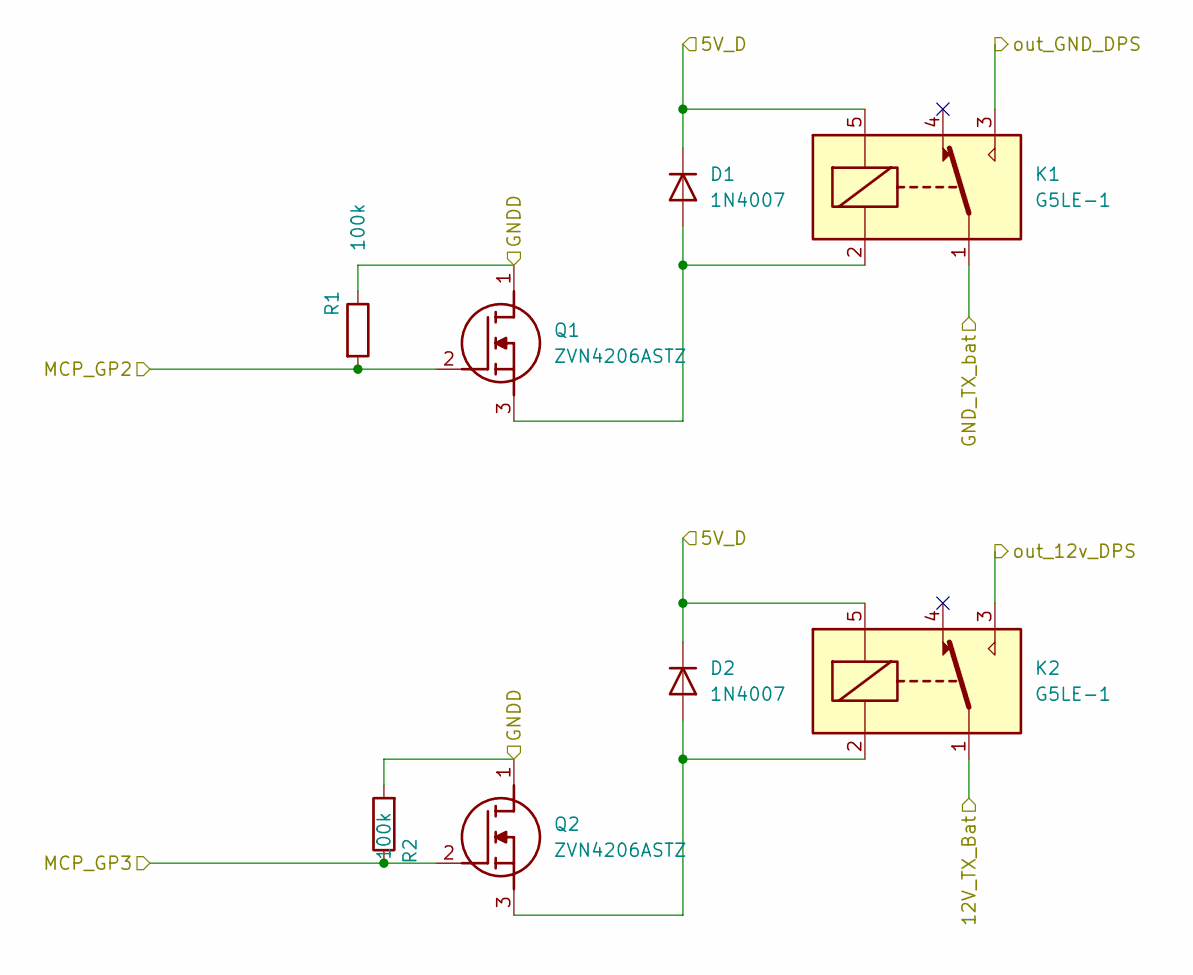
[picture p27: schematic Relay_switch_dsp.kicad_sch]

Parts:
D1, D2: 1N4007; D_DO-41_SOD81_P10.16mm_Horizontal
K1, K2: G5LE-1; Relay_SPDT_Omron-G5LE-1
Q1, Q2: ZVN4206ASTZ; TO-92L_Wide; Manufacturer_Part_Number ZVN4206ASTZ; Mouser Part Number 522-ZVN4206ASTZ
R1, R2: 100k; R_Axial_DIN0207_L6.3mm_D2.5mm_P7.62mm_Horizontal

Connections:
5VD: D1.1 (K), D2.1 (K), K1.5, K2.5; also elsewhere on the board
+12V_TX_bat: K2.1; also elsewhere on the board
/Relay_switch_DPS/out_12v_DPS: K2.3; also elsewhere on the board
/Relay_switch_DPS/out_GND_DPS: K1.3; also elsewhere on the board
GNDD: Q1.1 (D), Q2.1 (D), R1.1, R2.2; also elsewhere on the board
GND_TX_bat: K1.1; also elsewhere on the board
GP2: Q1.2 (G), R1.2; also elsewhere on the board
GP3: Q2.2 (G), R2.1; also elsewhere on the board
unnamed: D1.2 (A), K1.2, Q1.3 (S)
unnamed: D2.2 (A), K2.2, Q2.3 (S)

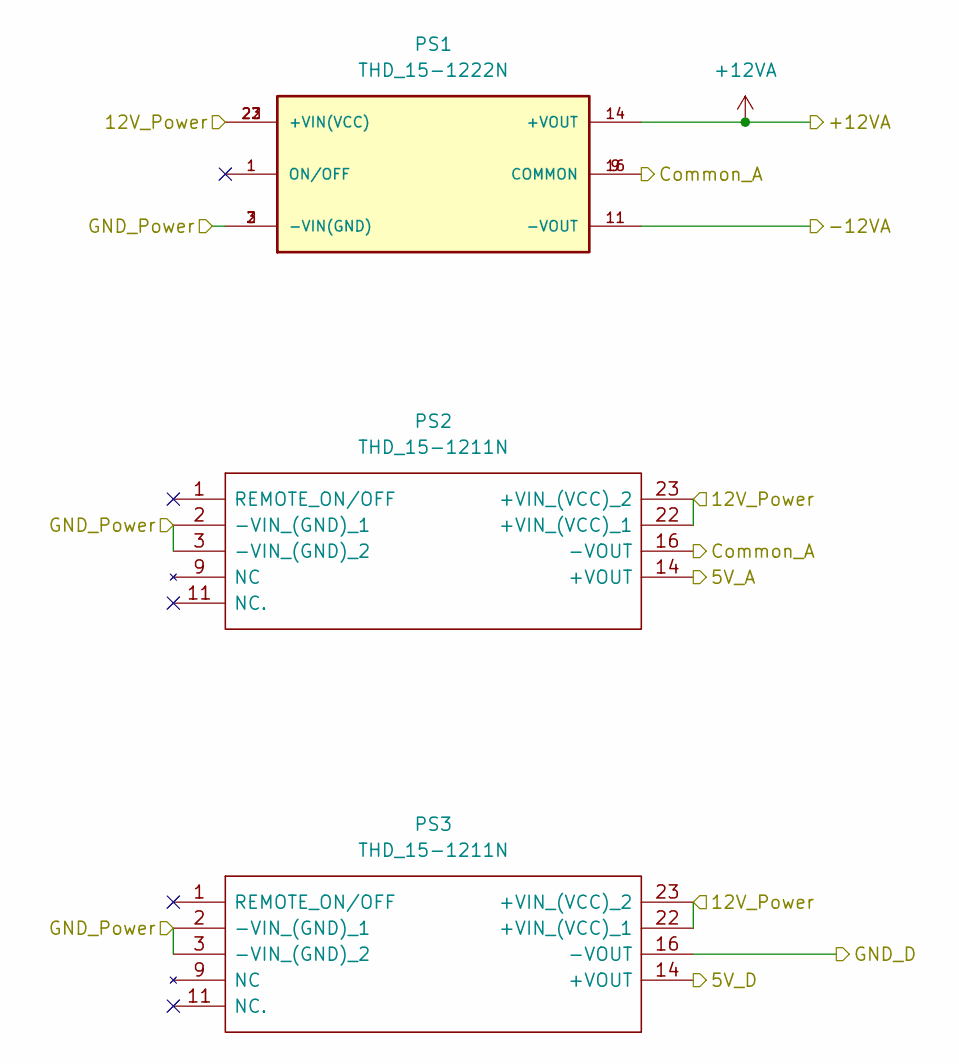
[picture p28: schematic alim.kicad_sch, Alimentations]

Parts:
PS1: THD_15-1222N; CONV_THD_15-1222N; PARTREV July 27, 2020
PS2, PS3: THD_15-1211N; THD151211N; Manufacturer_Part_Number THD 15-1211N; Mouser Part Number 495-THD15-1211N

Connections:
5VA: PS2.14 (+VOUT); also elsewhere on the board
5VD: PS3.14 (+VOUT); also elsewhere on the board
+12V: PS1.22 (+VIN(VCC)), PS1.23 (+VIN(VCC)), PS2.22 (+VIN_(VCC)_1), PS2.23 (+VIN_(VCC)_2), PS3.22 (+VIN_(VCC)_1), PS3.23 (+VIN_(VCC)_2); also elsewhere on the board
+12V_A: PS1.14 (+VOUT); also elsewhere on the board
-12V_A: PS1.11 (-VOUT); also elsewhere on the board
GNDA: PS1.9 (COMMON), PS1.16 (COMMON), PS2.16 (-VOUT); also elsewhere on the board
GNDD: PS3.16 (-VOUT); also elsewhere on the board
GNDPWR: PS1.2 (-VIN(GND)), PS1.3 (-VIN(GND)), PS2.2 (-VIN_(GND)_1), PS2.3 (-VIN_(GND)_2), PS3.2 (-VIN_(GND)_1), PS3.3 (-VIN_(GND)_2); also elsewhere on the board

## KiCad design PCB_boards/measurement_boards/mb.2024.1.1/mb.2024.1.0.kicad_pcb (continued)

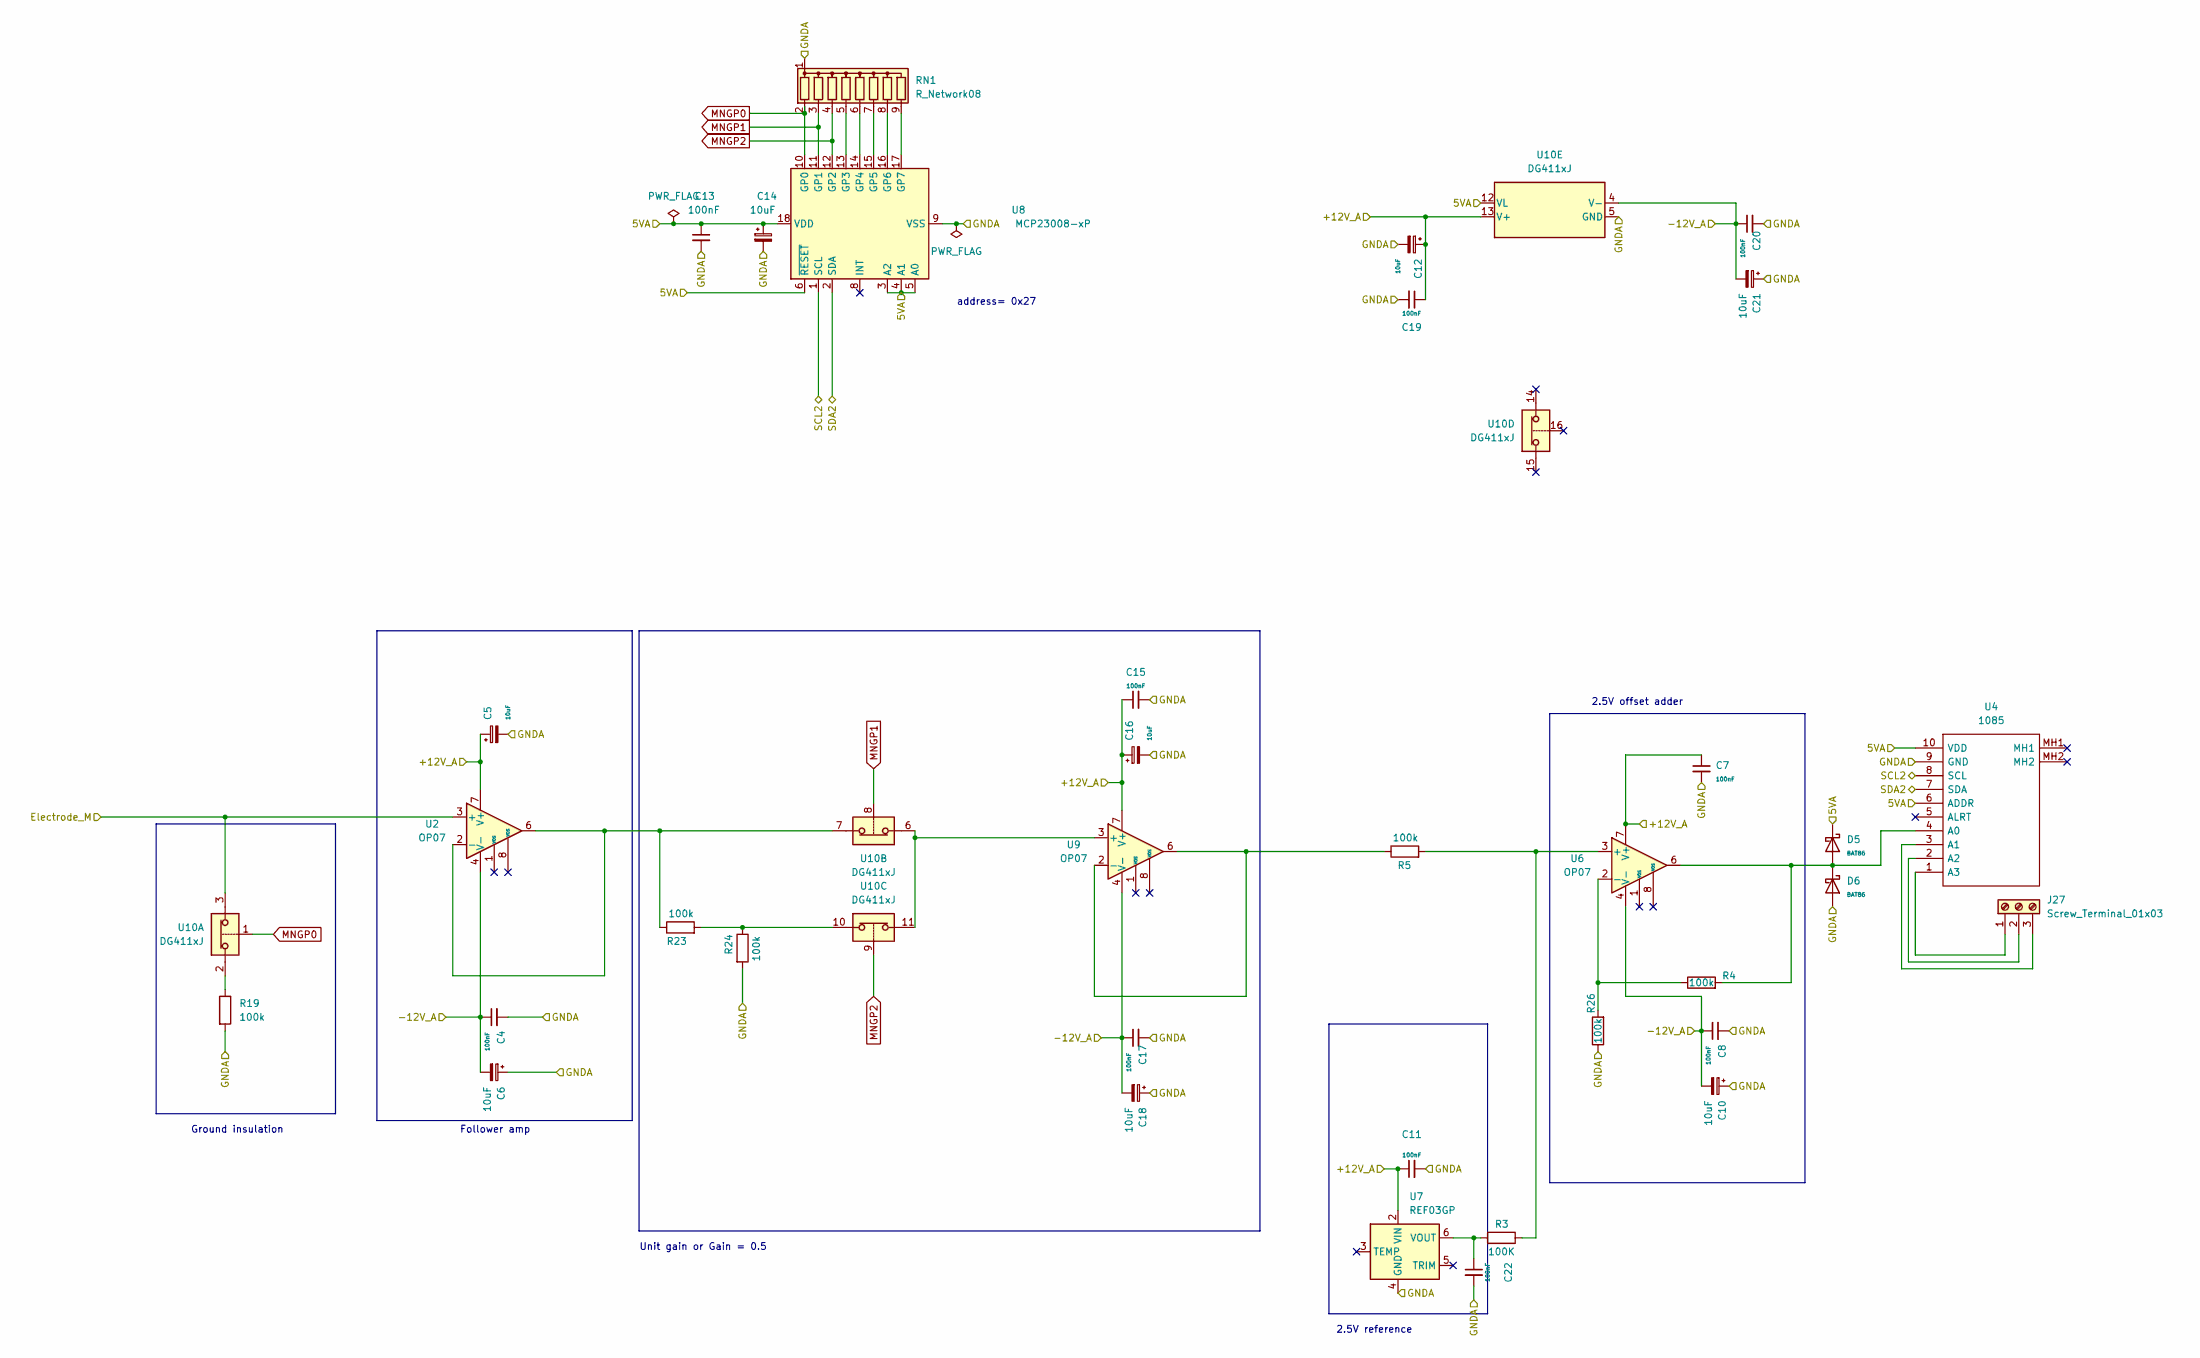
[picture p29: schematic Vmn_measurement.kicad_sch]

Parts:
C4, C7, C8, C11, C13, C15, C17, C19, C20, C22: 100nF; C_Disc_D8.0mm_W2.5mm_P5.00mm
C5, C6, C10, C12, C14, C16, C18, C21: 10uF; CP_Radial_D6.3mm_P2.50mm
D5, D6: BAT86; D_DO-35_SOD27_P7.62mm_Horizontal
J27: Screw_Terminal_01x03; TerminalBlock_bornier-3_P5.08mm
R3: 100K; R_Axial_DIN0207_L6.3mm_D2.5mm_P7.62mm_Horizontal
R4, R5, R19, R23, R24, R26: 100k; R_Axial_DIN0207_L6.3mm_D2.5mm_P7.62mm_Horizontal
RN1: R_Network08; R_Array_SIP9
U2, U6, U9: OP07; DIP-8_W7.62mm
U4: 1085; Manufacturer_Part_Number 1085; Mouser Part Number 485-1085
U7: REF03GP; DIP-8_W7.62mm
U8: MCP23008-xP; DIP-18_W7.62mm
U10: DG411xJ; DIP-16_W7.62mm

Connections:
5VA: C13.1, C14.1, D5.1 (K), U4.6 (ADDR), U4.10 (VDD), U8.3 (A2), U8.4 (A1), U8.5 (A0), U8.6 (~RESET), U8.18 (VDD), U10.12 (VL); also elsewhere on the board
+12V_A: C5.1, C7.1, C11.1, C12.1, C15.1, C16.1, C19.1, U2.7 (V+), U6.7 (V+), U7.2 (VIN), U9.7 (V+), U10.13 (V+); also elsewhere on the board
-12V_A: C4.1, C6.2, C8.1, C10.2, C17.1, C18.2, C20.1, C21.2, U2.4 (V-), U6.4 (V-), U9.4 (V-), U10.4 (V-); also elsewhere on the board
/Vmn_measurement/Electrode_M: U2.3 (+), U10.3; also elsewhere on the board
GNDA: C4.2, C5.2, C6.1, C7.2, C8.2, C10.1, C11.2, C12.2, C13.2, C14.2, C15.2, C16.2, C17.2, C18.1, C19.2, C20.2, C21.1, C22.2, D6.2 (A), R19.2, R24.2, R26.1, RN1.1 (common), U4.9 (GND), U7.4 (GND), U8.9 (VSS), U10.5 (GND); also elsewhere on the board
MNGP0: RN1.2 (R1), U8.10 (GP0), U10.1
MNGP1: RN1.3 (R2), U8.11 (GP1), U10.8
MNGP2: RN1.4 (R3), U8.12 (GP2), U10.9
unnamed: D5.2 (A), D6.1 (K), R4.2, U4.4 (A0), U6.6
unnamed: J27.1, U4.1 (A3)
unnamed: J27.2, U4.2 (A2)
unnamed: J27.3, U4.3 (A1)
unnamed: R19.1, U10.2
unnamed: R23.2, R24.1, U10.10
unnamed: RN1.5 (R4), U8.13 (GP3)
unnamed: RN1.6 (R5), U8.14 (GP4)
unnamed: RN1.7 (R6), U8.15 (GP5)
unnamed: RN1.8 (R7), U8.16 (GP6)
unnamed: RN1.9 (R8), U8.17 (GP7)
unnamed: R23.1, U2.2 (-), U2.6, U10.7
unnamed: R3.1, R5.2, U6.3 (+)
unnamed: R4.1, R26.2, U6.2 (-)
unnamed: C22.1, R3.2, U7.6 (VOUT)
unnamed: U9.3 (+), U10.6, U10.11
unnamed: R5.1, U9.2 (-), U9.6
SCL2: U4.8 (SCL), U8.1 (SCL); also elsewhere on the board
SDA2: U4.7 (SDA), U8.2 (SDA); also elsewhere on the board

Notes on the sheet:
Follower amp
address= 0x27
Ground insulation
2.5V reference
Unit gain or Gain = 0.5
2.5V offset adder

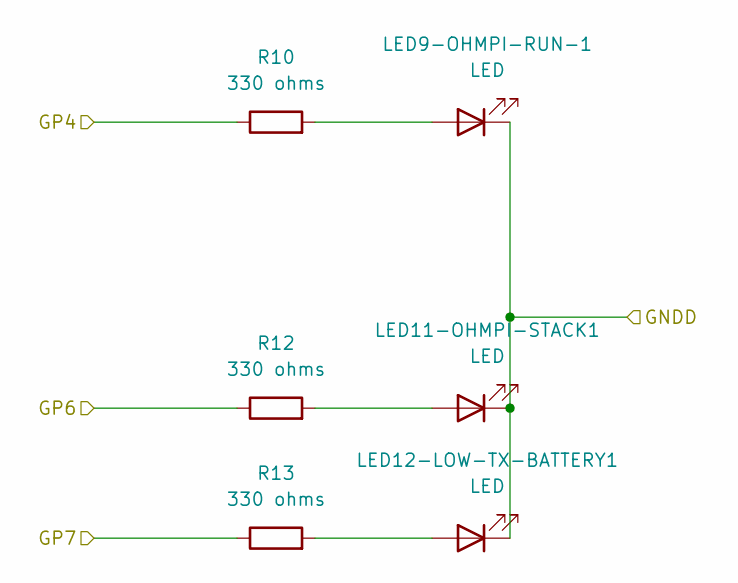
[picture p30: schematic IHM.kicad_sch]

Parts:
LED9-OHMPI-RUN-1, LED11-OHMPI-STACK1, LED12-LOW-TX-BATTERY1: LED; LED_D4.0mm
R10, R12, R13: 330 ohms; R_Axial_DIN0207_L6.3mm_D2.5mm_P7.62mm_Horizontal

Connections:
GNDD: LED9-OHMPI-RUN-1.1 (K), LED11-OHMPI-STACK1.1 (K), LED12-LOW-TX-BATTERY1.1 (K); also elsewhere on the board
GP4: R10.1; also elsewhere on the board
GP6: R12.1; also elsewhere on the board
GP7: R13.1; also elsewhere on the board
unnamed: LED9-OHMPI-RUN-1.2 (A), R10.2
unnamed: LED11-OHMPI-STACK1.2 (A), R12.2
unnamed: LED12-LOW-TX-BATTERY1.2 (A), R13.2

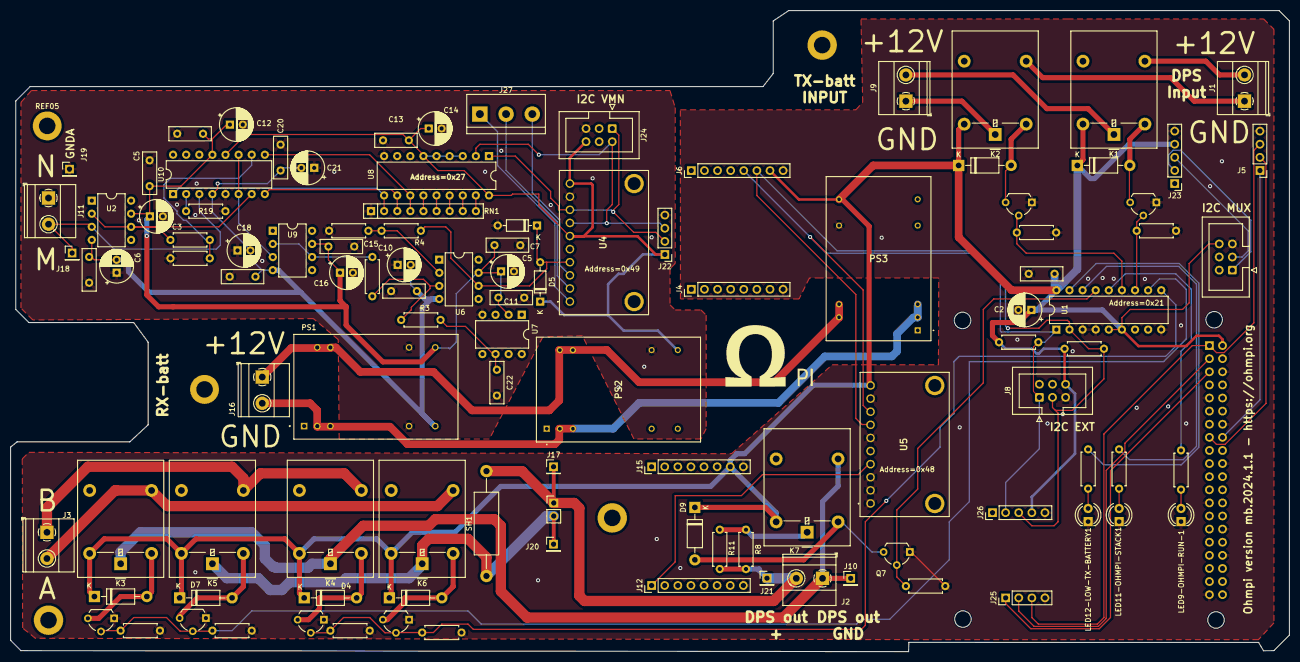
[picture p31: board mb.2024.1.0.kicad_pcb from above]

Board: 2 copper layers, 247.8 x 124.2 mm, 116 parts (1 on the bottom side), 69 nets.

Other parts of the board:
C3, C5#2: 10uF; CP_Radial_D6.3mm_P2.50mm
REF00, REF01, REF2, REF03: MountingHole_3.2mm_M3
REF04, REF05: MountingHole_3.2mm_M3_DIN965_Pad

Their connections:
+12V_A: C3.1, C5#2.1; also elsewhere on the board
GNDA: C3.2, C5#2.2; also elsewhere on the board

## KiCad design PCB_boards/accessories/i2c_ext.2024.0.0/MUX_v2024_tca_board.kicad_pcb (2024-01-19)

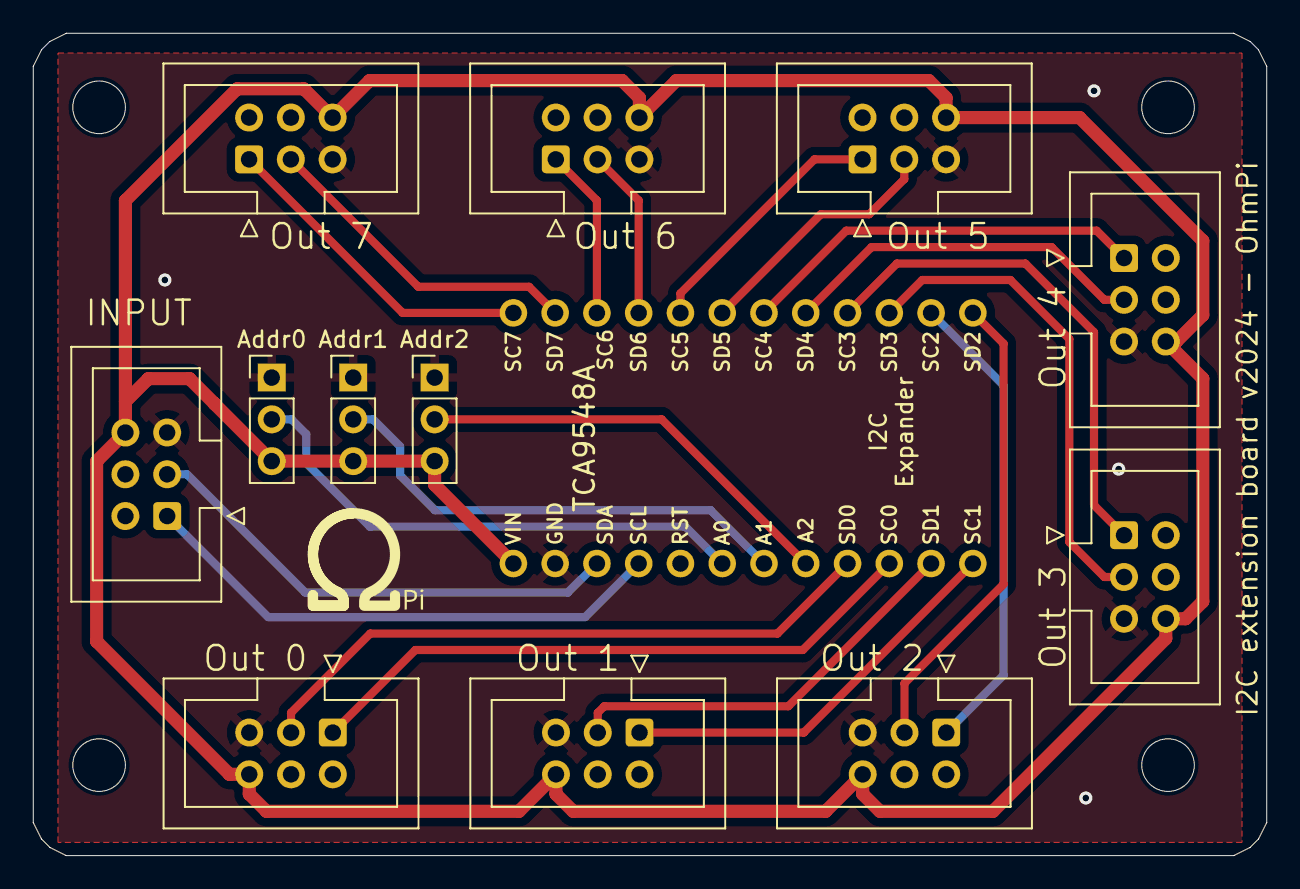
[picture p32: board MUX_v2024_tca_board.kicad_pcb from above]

Board: 2 copper layers, 75.0 x 50.0 mm, 14 parts (0 on the bottom side), 23 nets.

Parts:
Addr0: Addr0; PinHeader_1x03_P2.54mm_Vertical
Addr1: Addr 1; PinHeader_1x03_P2.54mm_Vertical
Addr2: Addr 2; PinHeader_1x03_P2.54mm_Vertical
J1, J2, J3, J4, J5, J6, J7, J8, J9: I2C; IDC-Header_2x03_P2.54mm_Vertical
JP1, JP3: HEADER-1X12; 1X12_ROUND

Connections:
+5V: Addr0.3 (B), Addr1.3 (B), Addr2.3 (B), J1.6, J2.6, J3.6, J4.6, J5.6, J6.6, J7.6, J8.6, J9.6, JP3.1
/0SCL: J2.1, JP3.10
/0SDA: J2.3, JP3.9
/1SCL: J3.1, JP3.12
/1SDA: J3.3, JP3.11
/2SCL: J9.1, JP1.2
/2SDA: J9.3, JP1.1
/3SCL: J8.1, JP1.4
/3SDA: J8.3, JP1.3
/4SCL: J7.1, JP1.6
/4SDA: J7.3, JP1.5
/5SCL: J6.1, JP1.8
/5SDA: J6.3, JP1.7
/6SCL: J5.1, JP1.10
/6SDA: J5.3, JP1.9
/7SCL: J4.1, JP1.12
/7SDA: J4.3, JP1.11
/A0: Addr0.2 (C), JP3.6
/A1: Addr1.2 (C), JP3.7
/A2: Addr2.2 (C), JP3.8
/INPUTSCL: J1.1, JP3.4
/INPUTSDA: J1.3, JP3.3
GNDD: Addr0.1 (A), Addr1.1 (A), Addr2.1 (A), J1.5, J2.5, J3.5, J4.5, J5.5, J6.5, J7.5, J8.5, J9.5, JP3.2

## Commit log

2023-11-29 change the architecture of the measurement board section
2023-11-29 update documentation mb.rst to describe board specifications
2023-12-01 update doc
    [sch.csv]
2023-12-01 Fixes issue on delay for selecting samples
2023-12-01 Places tx_volt print outputs in exec_logger.debug
2023-12-01 Updates current setting on dps
2023-12-03 update image for meseaurement board 2024.0.2
    [MUX_board_2023.csv, MUX_board_list_2_xx.csv]
2023-12-05 Adds self.electrodes in mux
2023-12-11 updates select samples to avoid pulse not recorded due to Rpi lag
2023-12-12 updates ohmpi for voltage_adjustable
2023-12-13 Adds MUX 2024 designs
    [Addresses_table.xlsx, MUX_1_relay.kicad_sch, MUX_settings.csv, addresses_table_2roles.csv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]
2023-12-13 Updates MUX.2024.0.1 design
    [mux.2024.0.1.kicad_pcb]
2024-01-08 update documentation
    [mb.2024.0.2.kicad_pcb]
2024-01-10 generate GERBER file for mux 2023.0.2
    [mux.2023.0.1.fzz]
2024-01-10 generate GERBER file for mux 2023.0.X electrode connector
    [connector_16.fzz]
2024-01-19 updates I2C_ext board pcb
    [MUX_v2024_tca_board.kicad_pcb]
2024-01-22 adds ohmpi_measure led
2024-01-27 update rs_check function for couple of electrode
2024-01-27 review raspberry pi hardware description
2024-01-27 review MUX board
2024-01-27 review power supply for current injection
2024-01-28 update hardware description, describe all possibility to assemble ohmpi and correct the architecture of the hardware part
2024-01-28 update assemble ohmpi V2024
2024-01-28 updates mux 2024 doc
    [MUX_board_2024.csv]
2024-01-30 Improves mb2024 mounting instructions
2024-01-30 fixes issue in electrodes definition in mux_2023
2024-02-01 Casts the dps voltage as a float
2024-02-07 correction DPS, add dischage resistor, remove 63 warning on the schemtic, remove 7 errors in schematics change resistor designation, update pcb
    [Current_injection_and_measurement.kicad_sch, IHM.kicad_sch, Relay_switch_dsp.kicad_sch, Vmn_measurement.kicad_sch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]
2024-02-07 update measurement board
    [Current_injection_and_measurement.kicad_sch, Relay_switch_dsp.kicad_sch, mb.2024.0.2.kicad_pcb]
2024-02-15 adds event on voltage setter
2024-02-15 Adds check in dps voltage setter to avoid waiting if the voltage value is unchanged
2024-02-15 Adds check in dps voltage setter to avoid setting a voltage out of specs
2024-02-15 Removes print in pwrdps5005
2024-02-16 tries switch_mux and pwr_dps_on in thread
2024-02-16 sets power_latency to 0 on dps
2024-02-19 Fix doc screw terminals mux2024 + typo
    [MUX_board_2024.csv]
2024-02-20 Fix documentation (pic3 arrow missing, pic28/29 caption inverted, bom link 4.7k corrected, 3 OP27 insted of 4)
    [bom-ohmpi-mb2024.csv]
2024-02-20 Adds doc for OhmPi Lite assembling
2024-02-21 updates compute_tx_volt for returning voltage from battery config if pwr_batt and shift full_constant in compute_tx_volt
2024-02-21 updates compute_tx_volt for returning voltage from battery config if pwr_batt
2024-02-21 updates default voltage values for pwr_batt to allow fixed voltage other than 12V
2024-02-22 Shortening caption for header socket to avoid overzooming on image.
2024-02-27 updates voltage bounds for dps5005
2024-02-27 Adds sleep time as a function of difference between new and previous voltage to allow dps to reach desired voltage
2024-03-04 Adds logging info and warning for tx battery level on dps wake up
2024-03-10 last version of mesaurement board correction of web site adresse, named i2C EXT, I2C MUX and I2C Vmn, delete unused components
    [Current_injection_and_measurement.kicad_sch, IHM.kicad_sch, Relay_switch_dsp.kicad_sch, Vmn_measurement.kicad_sch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]
2024-03-10 change name 2024.0.3 to 2024.1.0
    [1085.stl, 1085.stp, Current_injection_and_measurement.kicad_sch, IHM.kicad_sch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]
2024-03-10 update diode 1n4007
    [Current_injection_and_measurement.kicad_sch, IHM.kicad_sch, Relay_switch_dsp.kicad_sch, Vmn_measurement.kicad_sch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]
2024-03-11 Adds MUX.2024.0.2 which updates ZVN4206 footprint
    [MUX_1_relay.kicad_sch, mux.2024.0.2.kicad_pcb, mux.2024.0.2.kicad_sch, mux.2024.0.2.xlsx]
2024-03-13 Update doc mux2024 (add warning for ZVN footprint error on PCB v2024.0.1)
2024-03-18 Update bom mb2024 to 3 OP27 instead of 4
    [bom-ohmpi-mb2024.csv]
2024-03-19 removes thread for switching mux and pwr simultanueously as vab needs to be computed before switching pwr on
2024-03-19 Adds filter_log
2024-03-20 adds sequence sampler and method to estimate optimal vab for sequence
2024-03-25 Adds contact resistor board
    [contact_resistor_test.kicad_pcb, contact_resistor_test.kicad_sch, test_values.xlsx]
2024-03-25 adds contact resistor board utils and example
2024-04-05 cleans prints
2024-04-05 Adds the try except around config import to handle the case of not config.py in ohmpi as mentionnend in issue #172
2024-04-12 Adds power max to abstract hardware components specs
2024-04-12 Adds print for troubleshooting in run_measurement
2024-04-12 changes vmn_min and vmn_max units to volts
2024-04-12 removes prints from run_measurement
2024-05-24 Adds reference_circuit board PCB
    [reference_circuit.kicad_pcb, reference_circuit.kicad_sch]
2024-05-28 Removes unnecessary prints"
2024-06-26 Add manual check for mb2024
    [mb2024-test.csv]
2024-06-26 Add mux2024 hardware test
    [mb2024-test.csv, mux2024-test.csv]
2024-06-26 Add drawing of IDC connector difference mux2024/mux2023
2024-06-26 Update hardware check (mb2024, mux2024)
    [MUX_board_2023.csv, MUX_board_2024.csv, bom-ohmpi-mb2024.csv, mb2024-test-sc.csv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]
2024-06-26 Removes unwanted prints
2024-06-26 Adds prints to debug
2024-06-26 Add pwr layout drawing
    [bom-ohmpi-mb2024.csv]
2024-06-26 Fix OhmPi in install_resipy.sh + Add max 48 mA note in troubleshooting
2024-06-26 Updates power doc
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2024-06-28 Updates doc
    [strategies.ods]
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2024-07-01 Update BOM mux2024 and format
    [MUX_board_2024.csv, mb_2024_bom.csv]
2024-07-04 measurement board pads and track correction for THD
    [1085.stl, 1085.stp, Current_injection_and_measurement.kicad_sch, IHM.kicad_sch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]
2024-07-04 update version number on the PCB
    [mb.2024.1.0.kicad_pcb]
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2024-08-07 Fix mux2024 pcb missing R10-gate ZVN connection
    [mux.2024.0.2.kicad_pcb]
2024-08-07 Updates zone on MUX_2024.0.2 pcb
    [mux.2024.0.2.kicad_pcb]
2024-08-12 Add warning for soldering rpi header on under side of PCB + fix two -> three idc 6 pins
2024-08-20 Add V11 test (2.5V on A0 ADS voltage) to mb2025 checks
    [mb2024-test.csv]
2024-09-18 Updates zone on MUX 2024 - no major change
    [mux.2024.0.2.kicad_pcb]
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2024-09-18 fixes current_overload register to address #229
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2024-10-02 Update link to IDC socket and plug for mux2023
    [MUX_board_2023.csv]
2024-10-07 Update relay mux2023 link with relay used in mux2024 (cheaper)
    [MUX_board_2023.csv]
2024-11-04 Reverts dph5005 voltage_max spec to 50.99V
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2024-11-06 Add map
    [map.csv]
2024-11-06 Adds the interactive map module
    [map.csv]
2024-11-07 Add map to system overview
    [map.csv]
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2024-11-11 Update bom list for mb2024
    [mb_2024_bom.csv]
2024-11-13 Fixes typo and changes component link in MUX2024
    [MUX_board_2024.csv]
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2024-11-29 Update mb2024 checks
    [mb2024-test.csv]
2025-01-20 solves issue #271
    [MUX_1_relay.kicad_sch, mux.2024.0.3.kicad_pcb, mux.2024.0.3.kicad_sch, mux.2024.0.3.xlsx]
2025-01-21 solves issue #271 by enlarging zones and removing via
    [mux.2024.0.3.kicad_pcb]
2025-01-21 removing MUX.2024.0.2 #271
    [MUX_1_relay.kicad_sch, mux.2024.0.2.kicad_pcb, mux.2024.0.2.kicad_sch, mux.2024.0.2.xlsx]
2025-01-22 adds new reference circuit #260
    [reference_circuit.2025.0.0.kicad_pcb, reference_circuit.2025.0.0.kicad_sch]
2025-01-29 Updates docs on MUX board v2024 after assembly
    [mux2024-test-sc.csv, mux2024-test.csv]
2025-01-29 Fixes I2C input on mux2024-text.jpg and SCK in table
    [mux2024-test.csv]
2025-02-11 Fix mb2024 test (no continuity with SDA/SCL from current click) + Add current debugging
    [mb2024-test.csv]
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2025-02-13 Add warning for failed communication with power supply (inside ohmpihardware)
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2025-03-28 Add ohmpi lite 16
    [base.dxf, top.dxf]
2025-03-29 Update bom in doc
    [base.dxf, top.dxf]
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2025-03-31 Update doc ok
    [mb2024-test.csv, mb_2024_bom.csv]
2025-04-01 corrects manual check table for mux 2024
    [mux2024-test-sc.csv]
2025-04-01 Update doc mux2024-test
    [mux2024-test.csv]
2025-04-03 Fix example from 'constant' to 'safe' in assembly doc
2025-04-07 updates ohmpi map
    [map.csv]
2025-04-16 Update maps with latest registrations
    [map.csv]
2025-05-12 Add test mux2024 idc and screw
    [mux2024-test-sc.csv]
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2025-09-08 Remove doc and add docs git submodule
    [MUX_board_2023.csv, MUX_board_2024.csv, MUX_board_list_2_xx.csv, MUX_board_list_2_xx.xlsx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]
2025-09-11 Add correct gerber for mb2024.1.1
    [mb.2024.0.2-B_Paste.gbr, mb.2024.0.2-F_Cu.gbr, mb.2024.0.2-F_Paste.gbr, mb.2024.0.2-NPTH-drl_map.gbr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]
2026-01-12 Fixes version of library adafruit-circuitpython-ads1x15 in requirements.txt #311
